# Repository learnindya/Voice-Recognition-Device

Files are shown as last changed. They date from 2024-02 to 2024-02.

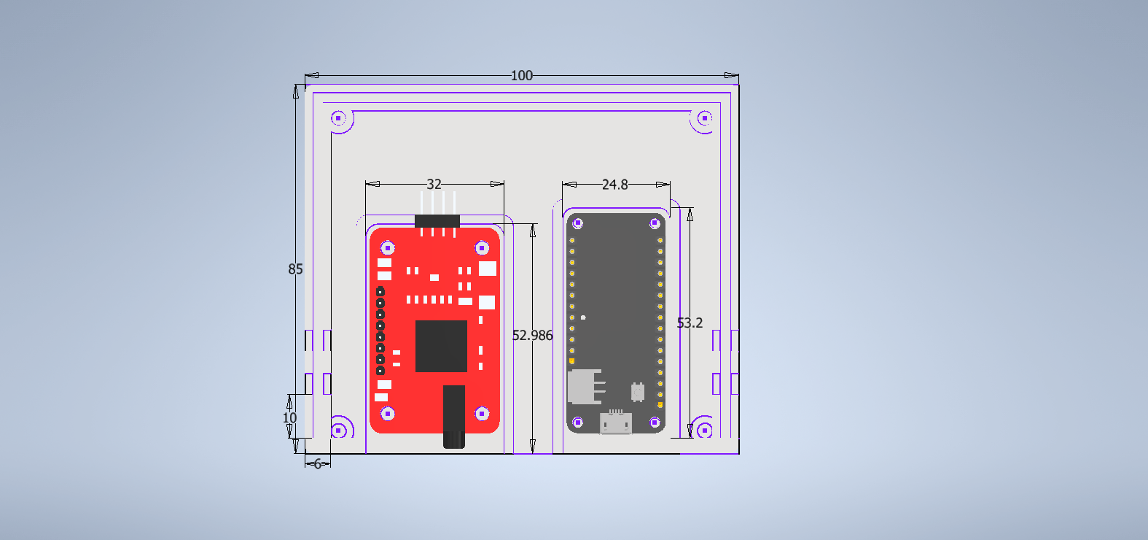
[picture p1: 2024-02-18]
3D drawing/Assembly2 b.png

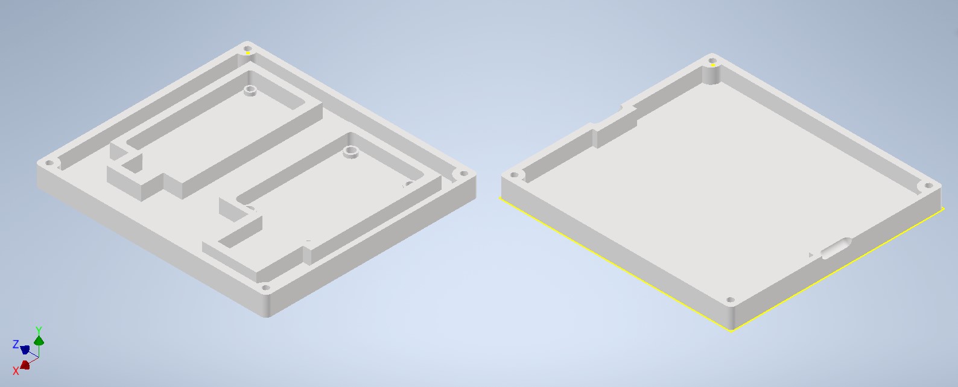
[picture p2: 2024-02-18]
3D drawing/Initial design.jpg

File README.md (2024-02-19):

# Voice-Recognition-Device
Wireless Voice Recognition Interface to Assist People with Tetraplegia to Control their Environment

## Problem
A switch is an essential tool in enabling access to assistive technologies and devices (e.g. Wheelchair controls, mouse clicks on a PC, switch control of electronics, etc.)
Current switch solutions have limitations: Complex mounting. Intrusive. Fragile.
Assistive Technology Manager at Aspire UK wanted to increase the options of accessible switch.

### Requirements from user:
**User Profile**
- Person with tetraplegia 
- No physical movement below neck 
- No speech impairment 
- May be ventilated 
- Assume there is movement of the head but that any head movement will be being used to move a mouse pointer 
- No cognitive impairment

**User Environment**
- Hospital, office
- Home
- Outdoors
- In wheelchair 

**User Acceptance**
- Un-obtrusive, wearable 
- Easy to understand and learn, intuitive to use 
- Minimal set-up needed. Promotes independence. 
- Robust

## Goal
Design a device that enables a person with tetraplegia to trigger a switch action.

## Procedure
1. Send questionnaire and conduct short interview to understand detailed user requirements.
2. Design the electrical diagram, program the modules
3. Assemble the casing and overall device
4. Record instructions
7. Measure the performance
   * Different subjects
   * Different length of commands
   * Different environments
   * Different distance from computer

## Result
- Response to short commands:



Accuracy, sensitivity, precision, prevalence and false positive rate were calculated. For the group testing their own voice (blue column) all values were above 98%. Meanwhile, the result from testing the other’s voice had lower results for all the parameters, and a decrease in respect to increasing distance was visible.

- Response to longer commands:



There was a decrease in all parameters for all subjects compared to short commands. The highest value for testing own’s voice was 94.67%.

- Different environments:



- Different distance from computer:



## Summary
- Price below 100£
- Performance in different environments: Only 6% difference in accuracy and sensitivity
- Battery life 6 hours
- Compatibility with iOS, Windows
- Wireless
- Trigger 6 actions

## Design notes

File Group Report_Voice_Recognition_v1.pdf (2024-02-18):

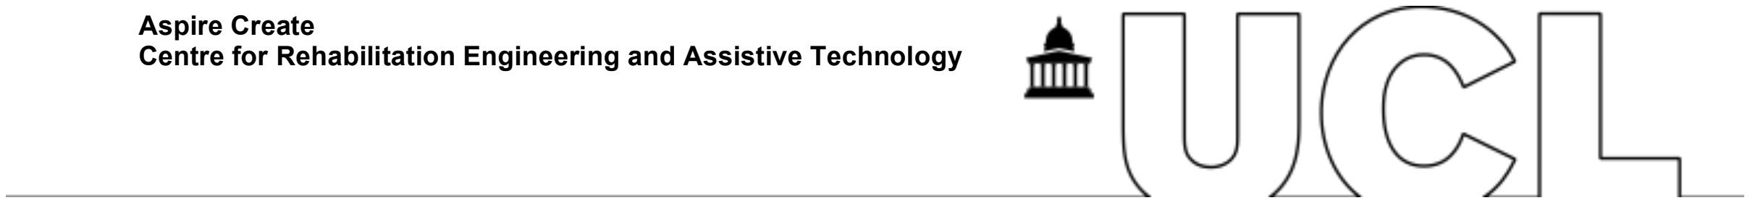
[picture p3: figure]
Aspire Create

University College London
RNOH, Brockley Hill, Stanmore, HA7 4LP, UK www.ucl.ac.uk/aspire-create

Centre for Rehabilitation Engineering and Assistive Technology

# Coursework Submission Coversheet

Student Number (not name!):
18149489, 19153381, 19119482, 19120072

Module Code:

### SURG0094: Group Research Projects

Coursework Title:

### Group Report

### Wireless Voice Recognition Interface to Assist People with Tetraplegia to Control their Environment

Submission Deadline:
11/12/2019 4:00 pm

Word count (include all sections except references/bibliography and appendices. Exclude footnotes, tables, figures, captions, references/bibliography and appendices):
2723

Feedback Request (optional). Please indicate any area(s) of your coursework submission upon which you would particularly like feedback:

NB: I confirm that by submitting this piece of coursework, I have read and understood the UCL statements and guidelines concerning plagiarism.

## UCL Policy on Plagiarism UCL Policy on Late Submission of Coursework

If you are unable to submit on-time due to extenuating circumstances (EC), please refer to

## the UCL Policy on Extenuating Circumstances and contact you’re your programme

administrator as soon as possible.

## UCL Policy on Extenuating Circumstances

## Wireless Voice Recognition Interface to Assist People with Tetraplegia to Control their Environment

A. Anindya (18149489)

1

, A. Khafizova (19120072)¹

, P. Chokpitiboon (19153381)¹

and F. Fries (19119482)¹

Abstract— Around 50% of patients suffering from tetraplegia prefer to stay at home relying on family members or carers to help them complete their daily activities. Despite the efforts to develop control interfaces to simplify their life, it is still hard to find effective products capable to access more than one device at the same time. In this project, we suggest the use of a customizable voice recognition module (VRM) combined with a Bluetooth board to access the computer and potentially a wheelchair. The VRM can store up to 15 commands, which combined, significantly increases the number of devices that can be controlled. In this work, the VRM was characterized to understand how to train the device and find the limitations of the product. The tests showed that the VRM is userdependent, reducing the likelihood of false positives, due to the noise from the environment or words said by someone else. It was also possible to connect to different computers (iOS, Windows) and perform daily tasks such as browsing the internet, opening an email and files, scroll pages up and down, etc. This device shows some interesting potential to aid people suffering from tetraplegia to complete multiple tasks, such as driving a wheelchair, controlling the environment or interface with computers and smartphones.

I. INTRODUCTION

Spinal cord injuries (SCI) affect around 40’000 people in the UK, and for the year 2013-2014, 51% of them are considered to be tetraplegics [1]. Tetraplegia occurs when the the upper cervical level of the spine (C1 to C5) gets damaged, resulting on impairment or complete loss of motor and sensory function below the neck. Due their condition, most of the patients opt to stay at home relying on family members or caregivers to assist them complete their daily activities [2].
Assistive technology is an emerging research area focusing on the development of devices to aid people with any kind of impairments and improve their quality of life. The muscles above the neck of patients suffering from tetraplegia are usually (fully) functional. Therefore, they use them to access computers or smartphones, drive wheelchairs or controlling the environment [3]. A series of switches to serve this purpose have reached the market [4], such as sip and puff switches [5], electromyography sensors [6] and mechanical switches. Moreover, methods like, eye tracking [7], tongue motion [8][9], head tracking [10], sniffing [11] and brain signals [12] have been studied by different research groups. The main problem lies in the management of a significant number of actions, for instance a wheelchair needs at least

1 All students are MSc candidates in Rehabilitation Engineering and Assistive Technologies at University College London (UCL). This project is part of the coursework for SURG0092 Assistive Technology Devices and Rehabilitation Robotics.

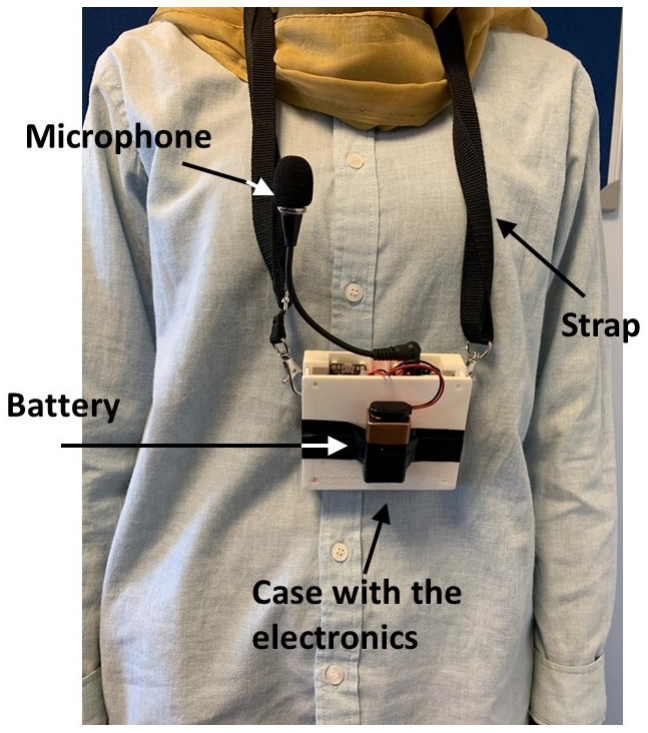
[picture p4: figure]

Fig. 1. User wearing the final prototype. The VRM and the Feather 32u4 are inside the 3D printed box.

five commands to be operated (forward, backwards, left and right, stop) [13]. Unfortunately, the aforementioned methods can saturate when more tasks are combined, thus the interest in more dynamic and efficient methods for hands-free completion of tasks.
An interface that has improved over the years if speech recognition, today it is possible to control (almost) every handheld or computer using speech recognition. However, the most recent devices controlled by voice require access to internet limiting the capabilities of the devices [13]. Nonetheless, voice represents a viable solution to provide patients suffering of tetraplegia with a control interface. Speech has already been used to control wheelchairs [14][15] and more effective algorithms have been develop [13] to enhance their performance. Thus, for this group project we propose the use of a commercial voice recognition module (VRM) capable of recording 15 different commands. The contributions of his work is the characterization of such module and the development of a wireless standalone device capable of aid people with upper limps paralysis to control a computer or a smart phone device. The device design will be described in section II, the methodology and results will be presented in sections III and IV, and the project will be discussed and concluded in sections V and VI respectively.

II. DEVICE DESIGN

A. User Requirements and Product Specifications

The intention was to design a user-oriented prototype, hence, potential end-users were interviewed about their ideas and preferences of the device. This indicated a need to obtain ethical approval before the start of the consultation. Main ethical considerations relate to users’ false expectations of the prototype and confidentiality of the collected data. Since the developed design is a prototype only, a user will not be able to take it home or start using it independently. The number of ethics application is 6860/001 and it was approved by University College London (UCL) Research Ethics Committee. To ensure confidentiality of the obtained data, it was used anonymously in the report. The user requirements were acquired by questionnaire method. There were two questionnaires, one for user and one for family, caregiver and clinician (Appendix ??, and were distributed by email. Due to time constraint, the questionnaires were filled by an assistive technology specialist. The user requirements are presented (Table I).

Parameter | Requirement
Cost Performance Battery Life Physical Design Compatibility Type of communication Minimum Actions | Below 100£ Reliable in different environments 2 to 3 days Inconspicuous iOS, Windows, Android Wireless Trigger 1 action

TABLE I

USER REQUIREMENTS

A set of device specifications listed below were derived from the user requirements:

- Arduino based hardware
- Capable to trigger multiple actions
- Customizable
- Capable to interface with different devices (computer, cellphone, wheelchair, home automation, etc.)
- HID Bluetooth communication protocol
B. Voice Recognition Module
1) Hardware: we purchased an Arduino compatible VRM(Geeetech Voice Recognition, Shenzhen Getech Technology Co.) for this prototype. An image can be seen in Fig. 2, the module can store up to 15 commands in three groups of 5 commands per group. The needed commands have to be recorded on the module first. The module has 4 pins (VCC, GND, Tx, and Rx) to be powered (5V) and to communicate (5V logic) with the environment.
2) Training the voice recognition device: the module is capable to record any kind of commands, as long as it is less than 1.3s long, can be a word or a sentence and it is not language specific. When recording the commands, the entire group has to be recorded at the same time (5 commands), to do so the module has to be accessed through a serial port, we used a UART to USB bridge (CP2102, Silicon Labs). Once the device is accesessed the commands can be recorded. The person recording the commands has to say each command twice to ensure repeatability. If the voice recognition device considers that both pronunciations were identical (or almost the same) the command will be stored, otherwise he will ask to repeat that specific command. The process is repeated for each command until the 5 of them are recorded. After a group is completed it is possible to record the other groups (it is not necessary to record all the commands).

Listing 1. Command examples
/ / Mouse r i g h t c l i c k
b l e . sendCommandCheckOK
( F ( ”AT+BleHi dM o u seB utt o n =R , c l i c k ” ) ) ;

/ / Mouse l e f t c l i c k
b l e . sendCommandCheckOK
( F ( ”AT+BleHi dM o u seB utt o n =L , c l i c k ” ) ) ;

/ / Double c l i c k
b l e . sendCommandCheckOK
( F ( ”AT+BleHi dM o u seB utt o n =L , d o u b l e c l i c k ” ) ) ;

/ / Drag and Drop
b l e . sendCommandCheckOK
( F ( ”AT+BleHi dM o u seB utt o n =L , h ol d , 5 0 0 ” ) ) ;

/ / Read e m ail
b l e . sendCommandCheckOK
( F ( ”AT+BLEHIDCONTROLKEY=EMAILREADER” ) ) ;
C. Electronic Circuit
1) Interface: The entire control interface is composed of different components as depicted in Fig 2. The voice recognition and the Feather have different power requirements, 5V and 3.3V respectively. Two batteries are used to power this prototype, a 9V alkaline battery and a 3.7 LiPo Battery. Therefore, they were not compatible, we solved this problem by adding a logic converter module (Sparkfun Electronics) that converts the 5V logic of the voice recognition to 3.3V logic of the feather, making the data processing possible. A buck converter (Sparkfun Electronics) was used to convert the 9V of the battery to 5V.
2) Software: the software was written in Arduino. When the VRM, detects a command it sends a value between 1-5 (one for each command). The Feather is constantly reading from the serial port, if a value comes in it is passed to a switch statement and the respective command is triggered.

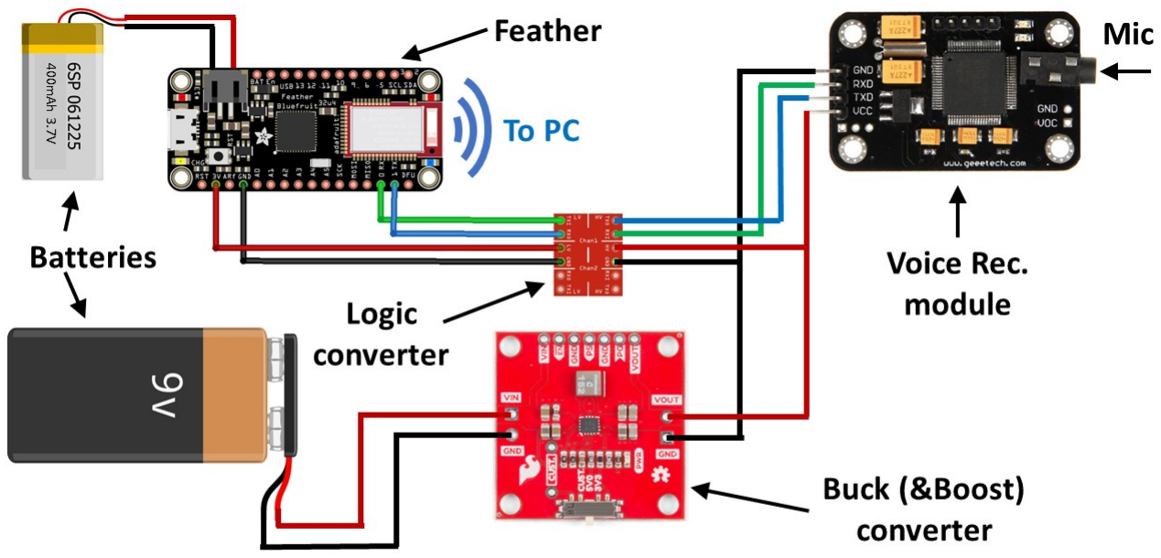
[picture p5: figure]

Fig. 2. Electric diagram of the device. An Feather 32u4 is connected to a VRMthrough a logic converter. The Feather is capable to connect to any Bluettoth device and control it using HID commands. This prototype uses two sources of power.

The used commands were chosen after the characterization,
and are presented in Listing 1:
D. Case Design
To protect the electronics a case comprising a base and a cover, was designed using Autodesk Inventor. On the base, there were two spaces for Feather and the voice recognition module, with adequate space for cables and battery (Fig. 3). The case and its cover was coupled by protruding the cover and extruding the case. There were also screw holes to hold them together. Two supports were made on the left and right sides of the base to attach a strap. Case was printed in Ultimaker 2+ Extended 3D Printer, using acrylonitrile butadiene styrene (ABS). The final product weighed 65 g.

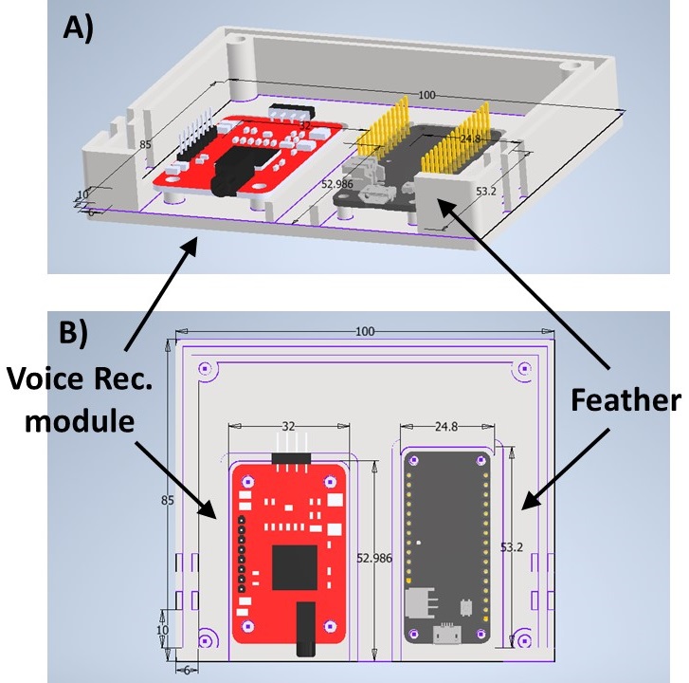
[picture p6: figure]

Fig. 3. CAD assembly of the device with dimensions (the cover is not depicted on this diagram). A) Isometric view. B) Top view.

III. EXPERIMENTS AND PROCEDURES

A. Characterization of the Voice Recognition Module
We performed a characterization of the voice recognition module, to understand its behavior and to be able to optimize the commands that will be implemented in the final prototype. We were interested in measuring the response of the device to different voices. Three subjects (S1, S2 and S3) participated in this experiment. First, the commands were recorded by S1, secondly, the response of the device to all the subjects was measured (including S1). Then the same commands were recorded by S2 and tested by all subjects and same for S3. A total of 15 measurements were taken for each experiment. The VRMwas connected to the computer through an Arduino, the response was displayed on the serial port and the result was recorded manually in Excel. The following experiments were performed:
1) Functional testing: the commands recorded for this experiment were the following:
- “Turn yellow”
- “Turn red”
- “Turn green”
- “Right”
- “Left”
Each command was given 5 times by each subject.
2) Commands length: the experiment was carried as described in the previous test, longer commands were recorded:
- “Turn yellow light on”
- “Turn red light on”
- “Turn green light on”
- “Make a right click”
- “Make a left click”
Each command was given 5 times by each subject.
B. Device Performance
The characterization served to optimize the commands of the final prototype. One subject recorded the commands and all the experiments were carried by that subject. The five commands chosen are sufficient to fully control a computer wirelessly using the device. Each command was given to the VRMand sent to the computer via Bluetooth (through the Feather). As a result an action was triggered on the computer. Same commands were used for the following experiments:
- ”Left mouse”
- ”Right click”
- ”Open file”
- ”Drag and drop”
- ”Email reader”
For all the test each command was given 5 times.
1) Noisy environments: the user repeated each command five times in the following environments:
- Classroom: the device was placed in a classroom with other people and the commands were tested while other people were speaking.
- Street: the device was tested outside the building in a street with cars and people.
- Coffee shop the switch was tested in a coffee shop with music playing and other people speaking.
- Bus stop: the device was taken to a bus stop and was tested with other cars and passengers passing.
- Bar: the device was tested in a relatively noisy environment with the music and other people speaking/screaming.
2) False Positives: the aim of this experiment was to try triggering false positives by giving commands similar to the ones above, two tests were carried:
- Similarity: following commands were given 5 times each:
– ”Left house”
– ”Right blick”
– ”Open smile”
– ”Dark and drop”
– ”Email speeder”
- Only one word of the command: following commands were given 5 times each:
– ”Mouse”
– ”Click”
– ”File”
– ”Drag”
– ”Email”
3) Distance between interface and controlled device: The final prototype was first tested at a distance of 1m and then at a distance of 2m from the computer to observe the strength of a bluetooth connection. Each command was given 5 times.

IV. RESULTS
A. Characterization
1) Functional Testing: the results of the experiment are presented in Fig. 4. Accuracy, sensitivity, precision, prevalence and false positive rate were calculated. For the group testing their own voice (blue column) all values were above 98%. Meanwhile, the result from testing the other’s voice had lower results for all the parameters, and a decrease in respect to increasing distance was visible.

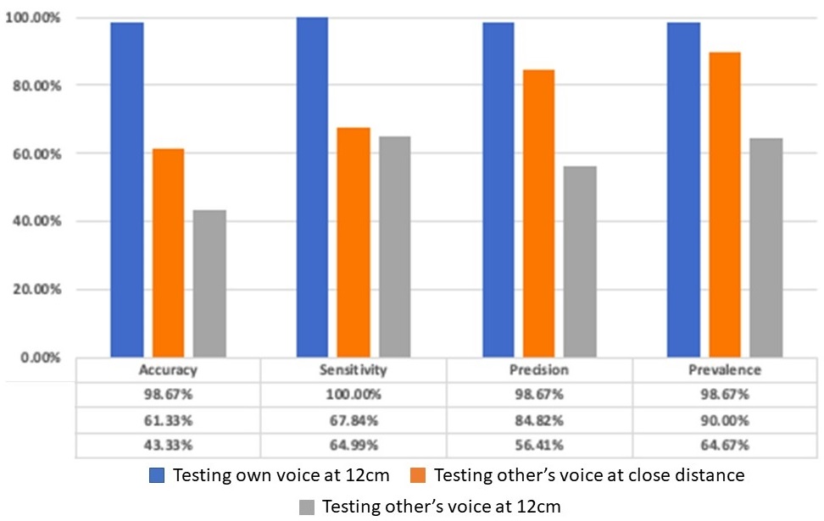
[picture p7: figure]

Fig. 4. Experiment to assess the functionality of the voice recognition module.

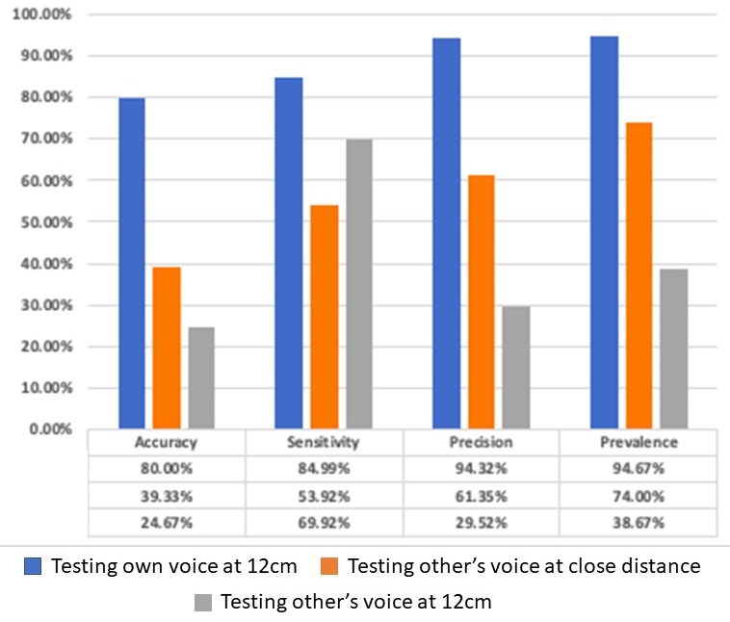
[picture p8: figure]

Fig. 5. Response of the VRMto longer commands.

2) Length of the commands: the results for longest commands are depicted in Fig. 5. The trends are similar to the ones shown in the previous experiment. However, there was a decrease in all parameters for all subjects. The highest value for testing own’s voice was 94.67%. The positives rates dropped significantly for the other’s voice results. Longer commands are more difficult to recognize.
B. Performance

The characterization experiments helped to define the commands for the final prototype. The following experiments were only performed by the subject that recorded the commands.
1) Noisy Environments: the environment experiment was performed and 6 non-controlled environments (street, coffee shop, bus stop, bar). The results of the silent room were compared to the average value from 6 non-controlled environments (Fig. 6). Classroom is slightly higher than that of the non-controlled group in term of accuracy and sensitivity (76% and 70.4% respectively) meanwhile there is no differ-

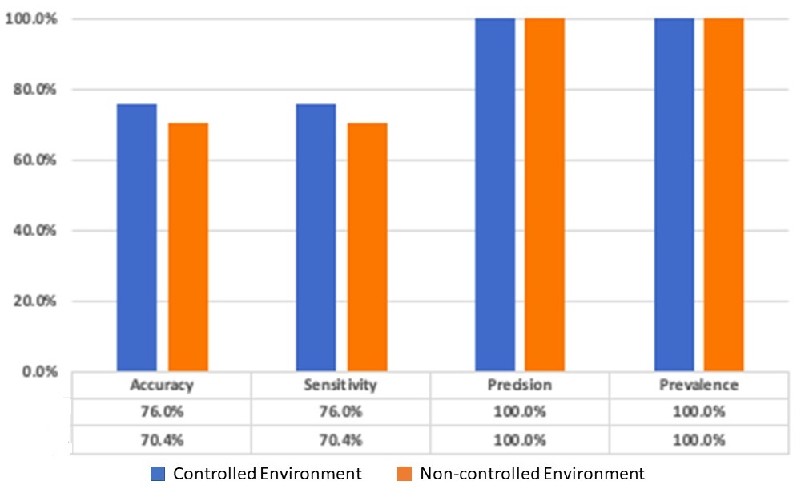
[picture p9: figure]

Fig. 6. Final prototype tested in 6 non controlled environments including street, coffee shop, bus stop, bar.

ence of the precision and prevalence (100% in both group). Trial done at bus stop has highest accuracy and sensitivity (80%) while lowest in the bar (48%). Environments with moderate noise do not affect the performance of the device. Whereas high noise results in an accurate behavior.

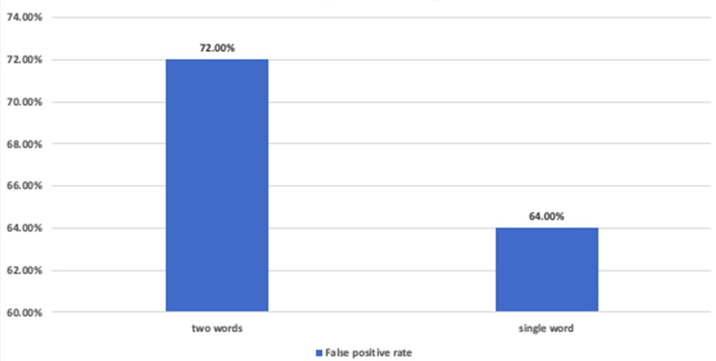
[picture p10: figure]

Fig. 7. After the commands were established. Similar words were given to the edvice to test the sensibility to other or simmilar commands.

2) False Positives: The results of the experiment are depicted in Fig. 7. Two words using similar ending (except drag and drop) showed a higher error rate (72%) than the one of the single similar word (64%). The device is highly sensitive to words similar to the commands, even if only one word of the command is said, the VRMis likely to react.
3) Connection performance: The trial done in 1 metre distance has greater value of accuracy and sensitivity (92%) than the 2 metre trial (88%), whereas, the precision and prevalence reach 100% in both trials as shown in Fig. 8. The experiments show that distance influences the performance of the interface.
V. DISCUSSION
A. Electronic Circuit
A VRMavailable in the market was chosen for this project. Combined with an Arduino based board (Feather 32u4) with Bluetooth capabilities it was possible to develop a wireless interface to control the environment. A series of difficulties arose due the different power requirements of the boards. A logic converter had to be included and the

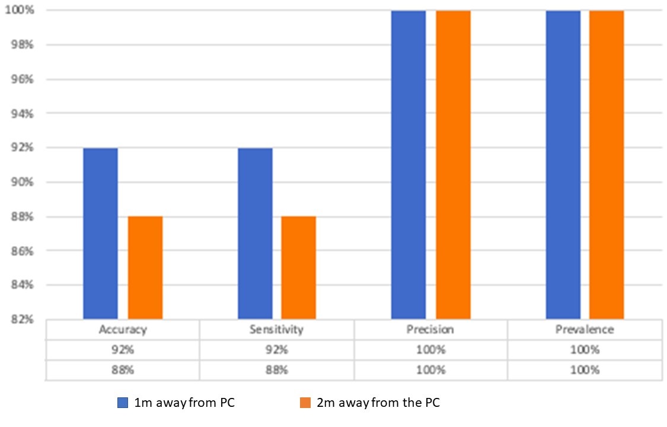
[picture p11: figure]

Fig. 8. User testing the device at different distances from the PC

prototype is currently powered by 2 batteries making the entire device bigger and inefficient. The electronics can be reduced to one printed circuit board (PCB) containing the logic converter and boost converter to power the entire device with one power source. Additionally the PCB would act as link between the Feather and the VRM.

B. Wireless Voice Recognition Interface
A series of tests were carried to study and understand the behavior of the VRM. The characterization experiments showed that shorter commands are more likely to be interpreted correctly by the VRM. Moreover, the device is significantly more responsive if the commands are recorded by the user itself. We also found out that commands need to differ from each other to increase the reliability.
Commands to interface with and control a computer were chosen after the characterization. The reliability of the device was shown in the environment experiment, where the device performed similar in environments with moderate noise. However, we also found out that the use of similar words (or commands) are likely to trigger the device. Reasons for this can be the quality of the microphone. In addition, the voice commands could be filtered to enhance the quality of the command received by the VRM.
The last experiment, indicated that an effective behavior is achieved if the user is close to the device that needs to be controlled. During the experiments we observed that the 3D printed case weakens the signal of the Feather. Therefore, the placement of the board is quite relevant. This can be solved by redesigning the case.

VI. CONCLUSION
Spinal cord injuries affect a significant number of people in the UK (and worldwide), and 51% of them suffer from tetraplegia. Thus, the need to create innovative devices for them to regain their independence and improve the quality of life. Plenty of mechanical switches and interfaces have reached the market, moreover research in this area is beeing supported and progress has been made. Nonetheless, the needs vary from patient to patient and is difficult to find a device suitable for every patient.

For this project we proposed the use of a commercially available VRM, capable to be trained with 15 different commands according to the individual’s requirements. Combined with a Bluetooth device (Feather) it was possible to create an interface to control electronic devices such as the computer hands-free. The experiments showed a high personalized device, likely to respond only to the user regardless of the environment capable to control the computer using 5 simple commands (right and left mouse click, drag and drop, double click and open email). In addition, the device is compatible with iOS and Windows without having to configure it.
In future work we will focus on the improvement of the electronic design, integrating everything into one PCB. This will allow the use of only one rechargeable LiPo battery making the device smaller. The software can also be improved, while it is possible to control the computer, more devices could be included such as wheelchair or the environment (lamps, TV etc.). To achieve this, we need to make use of the 15 commands valaible and be able to jump from one group to an other.

REFERENCES

[1] Spinal injuries association - spinal cord injury charity.
[2] Home page - NSCISC application.
[3] M N Sahadat, Arish Alreja, Nima Mikail, and Maysam Ghovanloo. Comparing the use of single vs. multiple combined abilities in conducting complex computer tasks hands-free. IEEE Transactions on Neural Systems and Rehabilitation Engineering, 2018.
[4] Giulio E. Lancioni, Jeff Sigafoos, Mark F. O’Reilly, and Nirbhay N. Singh. Use of microswitches in habilitation programs. In Assistive Technology, pages 11–40. 2013.
[5] Sip/puff switch.
[6] Sparkfun Electronics . MyoWare muscle sensor kit.
[7] Andreas Bulling and Hans Gellersen. Toward mobile eye-based human-computer interaction. IEEE Pervasive Computing, 2010.
[8] Salman Mohd Khan, Abid Ali Khan, and Omar Farooq. Selection of features and classifiers for EMG/EEG based upper limb assistive devices - a review. IEEE reviews in biomedical engineering, nov 2019.
[9] Lotte N S Andreasen Struijk, Bo Bentsen, Michael Gaihede, and Eugen R Lontis. Error-free text typing performance of an inductive intra-oral tongue computer interface for severely disabled individuals. IEEE Transactions on Neural Systems and Rehabilitation Engineering, pages 2094–2104, 2017.
[10] Ericka Janet Rechy-Ramirez, Huosheng Hu, and Klaus McDonald-Maier. Head movements based control of an intelligent wheelchair in an indoor environment. In 2012 IEEE International Conference on Robotics and Biomimetics (ROBIO). IEEE, 2012.
[11] Anton Plotkin, Lee Sela, Aharon Weissbrod, Roni Kahana, Lior Haviv, Yaara Yeshurun, Nachum Soroker, and Noam Sobel. Sniffing enables communication and environmental control for the severely disabled. Proceedings of the National Academy of Sciences of the United States of America, 2010.
[12] Tom Carlson and Jose del R. Millan. Brain-controlled wheelchairs: A robotic architecture. IEEE Robotics & Automation Magazine, 2013.
[13] Samuel Poirier, Francois Routhier, and Alexandre Campeau-Lecours. Voice control interface prototype for assistive robots for people living with upper limb disabilities. IEEE International Conference on Rehabilitation Robotics : [proceedings], 2019.
[14] Muhammad Tahir Qadri and Syed Ashfaque Ahmed. Voice controlled wheelchair using DSK TMS320C6711. In 2009 International Conference on Signal Acquisition and Processing. IEEE, 2009.
[15] Andrej Skraba, Andrej Kolozvari, Davorin Kofjac, and Radovan Stojanovic. Prototype of speech controlled cloud based wheelchair platform for disabled persons. In 2014 3rd Mediterranean Conference on Embedded Computing (MECO). IEEE, 2014.

### APPENDIX I SURVEY OF ASSISTIVE TECHNOLOGY FOR USER

### 1. What is your age? 20 and below

21 - 30
31 - 40

41 - 50
51 - 60

### above

### 2. Do you live alone or with other people? Living alone Living with people who provide assistance

3. Please indicate if you have difficulty in the following functions.

### Head movement e.g. nodding Eye twitching or blinking Mouth gripping Speaking

### 4. What is your current method to trigger a switch action (e.g. turning on computer)? ___________________________________________________________________ ___________________________________________________________________

### 5. Why did you decide to use the current method? ___________________________________________________________________ ___________________________________________________________________

### 6. What are your main factors in choosing an assistive technology to trigger a switch action? ___________________________________________________________________ ___________________________________________________________________

7. What kind of actions do you want to trigger by assistive technology? (e.g. texting,

### calling, sending commands to wheelchair) ___________________________________________________________________ ___________________________________________________________________

### 8. What do you think about using touch sensor to trigger a switch action? ___________________________________________________________________ ___________________________________________________________________

### 9. How often do you think the assistive device should be charged?

### _____________________________________________________hours/days

### 10. How much do you expect a touch sensor to cost? ___________________________________________________________________

11. What do you think of other assistive technology to trigger a switch action, e.g. voice

### recognition device? ___________________________________________________________________ ___________________________________________________________________

### SURVEY OF ASSISTIVE TECHNOLOGY FOR RELATIVES AND CLINICIANS

### 1. Please indicate who is completing this survey

### PaWieQW¶V famil\ Caregiver Doctor Other health professional, please specify: _________

### 2. Does tetraplegic patient require any assistance from you? Yes

If yes, please indicate the activities that require your assistance.

### ______________________________________________________________

No

### If no, is there any other form of assistance for the patient? ______________________________________________________________

### 3. Based on your experience, what is the best assistive technology to trigger a switch action? ___________________________________________________________________ ___________________________________________________________________

### 4. What do you consider in choosing an assistive technology to trigger a switch action for your patient/relative? ___________________________________________________________________ ___________________________________________________________________

### 5. What do you think about using touch sensor to trigger a switch action? ___________________________________________________________________ ___________________________________________________________________

### 6. How often do you think the assistive device should be charged?

### _____________________________________________________hours/days

### 7. How much do you expect a touch sensor to cost? ___________________________________________________________________

### 8. What do you think of other assistive technology to trigger a switch action, e.g. voice recognition device? ___________________________________________________________________ ___________________________________________________________________

### APPENDIX II SURVEY OF ASSISTIVE TECHNOLOGY FOR USER - FILLED

### 1. What is your age?

### x 20 and below x 21 - 30

x 31 - 40

### 2. Do you live alone or with other people? x Living alone

x 41 - 50 x 51 - 60

### x above

### x Living with people who provide assistance YES

3. Please indicate if you have difficulty in the following functions. x Head movement e.g. nodding x Eye twitching or blinking x Mouth gripping

### x Speaking

### 4. What is your current method to trigger a switch action (e.g. turning on computer)?

None

### 5. Why did you decide to use the current method?

n/a

### 6. What are your main factors in choosing an assistive technology to trigger a switch action?

Reliability and consistency. Inconspicuous.

7. What kind of actions do you want to trigger by assistive technology? (e.g. texting,

### calling, sending commands to wheelchair) Could be a number of possible uses. If it is easy to operate then I think it would have a wide application

### 8. What do you think about using touch sensor to trigger a switch action?

Depends on the way I would need to touch the device.

### 9. How often do you think the assistive device should be charged? Every 2-3 days hours/days

### 10. How much do you expect a touch sensor to cost?

<£100

11. What do you think of other assistive technology to trigger a switch action, e.g. voice

### recognition device?

OK providing it meets other criteria._

### SURVEY OF ASSISTIVE TECHNOLOGY FOR RELATIVES AND CLINICIANS - FILLED

### 1. Please indicate who is completing this survey

### x Patient’s family x Caregiver x Doctor x Other health professional, please specify: Assistive Technology Specialist

### 1. Does tetraplegic patient require any assistance from you? x Yes

If yes, please indicate the activities that require your assistance.

### Help with selection of Assistive devices for computer access

### x No If no, is there any other form of assistance for the patient?

### 3. Based on your experience, what is the best assistive technology to trigger a switch action? It depends in what context the switch is being used and what movement is available

to the user. With a high level injury there are limited options available.

### 4. What do you consider in choosing an assistive technology to trigger a switch action for your patient/relative?

Reliability and consistency oil operation. Inconspicuous.

### 5. What do you think about using touch sensor to trigger a switch action?

I am unable to touch with my hands - it would depend on how I am able to ac5vate it.

### 6. How often do you think the assistive device should be charged?

Once every 2-3 days would be best.

### hours/days

### 7. How much do you expect a touch sensor to cost?

If it does the job well than it will be worth a premium price. Typically switches should be <£100

### 8. What do you think of other assistive technology to trigger a switch action, e.g. voice recognition device?

Voice is fine, providing it is reliable and consistent and I can use independently.

### APPENDIX III RESULTS OF EXPERIMENT 1 TESTING SHORT COMMANDS BY DIFFERENT SUBJECTS: FUNCTIONAL TESTING

Test № | Voice owner | Tester | Testing distance | Trial | Commands
Turn yellow | Turn red | Turn green | Right | Left
1 | S1 | S1 | 12 cm | 1 | + | + | + | + | +
| | | | 2 | + | + | + | + | -
| | | | 3 | + | + | + | + | +
| | | | 4 | + | + | + | + | +
| | | | 5 | + | + | + | + | +
2 | S1 | S3 | 12 cm | 1 | -(red) | + | + | + | -
| | | | 2 | - | + | - | + | -
| | | | 3 | -(red) | + | - | - | -
| | | | 4 | -(red) | + | + | + | -
| | | | 5 | -(red) | + | - | + | -
3 | S1 | S2 | 12 cm | 1 | - | - | - | - | +
| | | | 2 | - | - | - | -(left) | +
| | | | 3 | - | - | - | -(greeen) | -(right)
| | | | 4 | - | - | - | -(yellow) | -(right)
| | | | 5 | - | - | - | -(left) | -(right)
4 | S1 | S3 | As close as possible | 1 | + | + | + | -(red) | +
| | | | 2 | + | + | -(noic e) | + | +
| | | | 3 | -(red) | + | + | + | +
| | | | 4 | - | + | + | + | -(right)
| | | | 5 | + | + | - | + | -(right)
5 | S1 | S2 | As close as possible | 1 | -(right) | -(left) | + | -(left) | -(right)
| | | | 2 | - | -(left) | + | -(yellow) | +
| | | | 3 | - | -(left) | -(left) | -(left) | +
| | | | 4 | -(left) | -(right) | -(left) | -(left) | +
| | | | 5 | - | -(right) | -(right ) | + | +
6 | S2 | S2 | 12 cm | 1 | + | + | + | + | +
| | | | 2 | + | + | + | + | +
| | | | 3 | + | + | + | + | +
| | | | 4 | + | + | + | + | +
| | | | 5 | + | + | + | + | +
7 | S2 | S3 | 12 cm | 1 | + | - | -(red) | + | -
| | | | 2 | - | - | + | - | -
| | | | 3 | - | - | + | + | -
| | | | 4 | - | - | + | - | -
| | | | 5 | - | - | + | + | -
8 | S2 | S1 | 12 cm | 1 | + | - | + | -(left) | +
| | | | 2 | - | - | + | -(left) | +

3 | - | - | + | -(left) | +
4 | - | - | + | -(left) | +
5 - | | -(green) | + | -(left) | +
9 | S2 | S3 | As close as possible | 1 | -(red) | + | + | + | +
| | | | 2 | + | + | -(red) | + | +
| | | | 3 | + | + | + | + | +
| | | | 4 | + | + | -(red) | + | +
| | | | 5 | + | + | + | + | +
10 | S2 | S1 | As close as possible | 1 | -(green) | + | + | -(left) | +
| | | | 2 | + | + | + | -(left) | +
| | | | 3 | + | + | + | + | +
| | | | 4 | + | + | + | -(left) | +
| | | | 5 | + | + | + | + | +
11 | S3 | S3 | 12 cm | 1 | + | + | + | + | +
| | | | 2 | + | + | + | + | +
| | | | 3 | + | + | + | + | +
| | | | 4 | + | + | + | + | +
| | | | 5 | + | + | + | + | +
12 | S3 | S2 | 12 cm | 1 | + | + | - | + | +
| | | | 2 | -(red) | + | -(left) | + | +
| | | | 3 | -(red) | -right | + | + | +
| | | | 4 | -(red) | -(left) | -(left) | + | +
| | | | 5 | -(red) | -(left) | + | + | +
13 | S3 | S1 | 12 cm | 1 | -(red) | + | -(red) | + | +
| | | | 2 | + | + | + | + | -(right)
| | | | 3 | + | - | - | + | -(right)
| | | | 4 | + | + | + | + | +
| | | | 5 + | | -(green) | + | + | +
14 | S3 | S2 | As close as possible | 1 | - | + | + | + | +
| | | | 2 | - | -(right) | + | -(left) | +
| | | | 3 | -(red) | -(left) | -(left) | -(left) | +
| | | | 4 | -(left) | -(left) | + | + | +
| | | | 5 | - | -(left) | -(red) | -(left) | +
15 | S3 | S1 | As close as possible | 1 | -(left) | + | -(red) | + | +
| | | | 2 | + | - | -(red) | + | +
| | | | 3 | + | - | -(red) | + | +
| | | | 4 + | | -(yellow ) | + | -(left) | -(right)
| | | | 5 | + | + | - | -(left) | +

### APPENDIX IV RESULTS OF EXPERIMENT 2 TESTING LONG COMMANDS BY DIFFERENT SUBJECTS: COMMAND LENGTHS

Test № | Voice owner | Tester | Testing distance | Trial | Commands
Turn the yellow light on | Turn the red light on | Turn the green light on | Make a right click | Make a left click
1 | S1 | S1 | 12 cm | 1 | -(red) | + | + | - (make a left click) | +
| | | | 2 | -(red) | + | + | - (make a left click) | +
| | | | 3 | -(red) | + | + | - (make a left click) | +
| | | | 4 | + | + | + | - (make a left click) | +
| | | | 5 | + | + | + | - (make a left click) | +
2 | S1 | S4 | 12 cm | 1 | - | + | - | - (make a left click) | +
| | | | 2 | - | - | - | - | -
| | | | 3 | - | - | - | - (make a left click) | -
| | | | 4 | + | - | + | - (make a left click) | +
| | | | 5 | - | - | - | - (make a left click) | +
3 | S1 | S2 | 12 cm | 1 | - | - | - | - | +
| | | | 2 | - | + | - | - | -
| | | | 3 | - | - | + | - | -
| | | | 4 | - | - | - | - | -
| | | | 5 | - | - | + | - | -
4 | S1 | S4 | As close as possible | 1 | - | - | -(make a right click) | - (make a left click) | +
| | | | 2 - | | -(make a left click) | -(make a left click) | - (make a left click) | +
| | | | 3 | + | -(green) | - | - (make a left click) | -
| | | | 4 - | | -(make a left click) | - | - (make a left click) | +
| | | | 5 | + | - | - | - (make a left click) | +
5 | S1 | S2 | As close as possible | 1 | -(make a left click) | -(green) | - | - (make a left click) | +
| | | | 2 | - | - | + | - (make a left click) | +
| | | | 3 | - | - | + | - | +
| | | | 4 | - | - | -(make a left click) | - (make a left click) | +

5 | - | - | +

### - (make a

left click) | +
6 | S2 | S2 | 12 cm | 1 | -(red) | + | + | + | +
| | | | 2 | + | + | + | + | +
| | | | 3 | + | + | + | + | +
| | | | 4 | - | -(green) | + | + | +
| | | | 5 | - | + | + | + | +
7 | S2 | S4 | 12 cm | 1 | -(green) | - | + | + | -(make a right click)
| | | | 2 - | | -(make a right click) | + | + | -(make a right click)
| | | | 3 | - | - | - | + | -(make a right click)
| | | | 4 | - | - | + | + | -
| | | | 5 | - | - | + | + | -
8 | S2 | S1 | 12 cm | 1 | -(red) | + | - | - | +
| | | | 2 | -(green) | + | - | - | +
| | | | 3 | - | + | - | - | +
| | | | 4 | - | - | - | - | -
| | | | 5 | -(red) | - | - | - | -
9 | S2 | S4 | As close as possible | 1 | -(red) | + | - | + | -(make a right click)
| | | | 2 -(red) | | -(make a right click) | -(make a right click) | + | -(make a right click)
| | | | 3 | - | + | -(make a right click) | + | -(make a right click)
| | | | 4 | - | + | -(make a right click) | + | -(make a right click)
| | | | 5 | - | + | + | + | +
10 | S2 | S1 | As close as possible | 1 | - | + | -(red) | + | -
| | | | 2 | - | + | -(red) | + | -(make a right click)
| | | | 3 | -(red) | + | + | + | -(make a right click)
| | | | 4 | - | + | -(red) | + | +
| | | | 5 | - | - | -(red) | + | +
11 | S4 | S4 | 12 cm | 1 | + | -(green) | + | - | +
| | | | 2 | + | + | + | + | +
| | | | 3 | + | + | + | + | +
| | | | 4 | + | + | + | + | +
| | | | 5 | + | - | + | + | +
12 | S4 | S2 | 12 cm | 1 | - | + | - | - | -
| | | | 2 | - | + | - | + | +

3 | - | - | - | - | -
4 | - | + | - | - | -
5 | - | + | - | - | -(make a right click)
13 | S4 | S1 | 12 cm | 1 | + | -(yellow) | -(yellow) | - | -
| | | | 2 | - | -(yellow) | -(yellow) | - | -
| | | | 3 | + | - | -(yellow) | - (make a left click) | -
| | | | 4 | + | - | -(yellow) | - | +
| | | | 5 | + | -(yellow) | - | - | +
14 | S4 | S2 | As close as possible | 1 | - | + | + | - | +
| | | | 2 | - | + | -(yellow) | + | +
| | | | 3 | - | + | - | + | +
| | | | 4 | - | + | - | - (make a left click) | -(make a right click)
| | | | 5 | + | + | - | + | +
15 | S4 | S1 | As close as possible | 1 | + | -(yellow) | -(yellow) | - | +
| | | | 2 | + | - | -(yellow) | - (make a left click) | -(make a right click)
| | | | 3 | + | -(yellow) | -(yellow) | - (make a left click) | +
| | | | 4 | + | -(yellow) | -(yellow) | - (make a left click) | -(make a right click)
| | | | 5 | + | -(yellow) | -(yellow) | - (make a left click) | +

### APPENDIX V RESULTS OF EXPERIMENT 3: ENVIRONMENTAL TESTING

### Quiet environment

### Street

№ trial | Left mouse | Right click | Open file | Drag and drop | Email reader
1 | + | + | - | + | +
2 | + | + | - | + | +
3 | + | + | + | + | +
4 | - | - | + | + | +
5 | + | - | - | + | +

### Coffee shop

№ trial | Left mouse | Right click | Open file | Drag and drop | Email reader
1 | + | + | - | + | +
2 | + | - | + | - | +
3 | + | - | + | - | +
4 | + | + | + | + | +
5 | + | - | + | + | +

### Bus stop

№ trial | Left mouse | Right click | Open file | Drag and drop | Email reader
1 | + | + | + | + | +
2 | + | + | + | + | +
3 | - | - | + | + | +
4 | - | - | + | + | -
№ trial | Left mouse | Right click | Open file | Drag n drop | Email reader
1 | + | + | + | + | +
2 | - | - | - | - | +
3 | + | - | + | + | +
4 | + | + | + | + | +
5 | + | - | + | + | +

5 | + | + | + | + | +

### Bar

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

### Classroom

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

### APPENDIX VI RESULTS OF EXPERIMENT 4: FALSE POSITIVE TESTING

№ trial | Left house | Right blick | Open smile | Dark and drop | Email speeder
1 | - | - | + | + | +
2 | - | + | + | + | +
3 | + | - | + | + | +
4 | + | - | - | + | +
5 | + | + | + | - | +
№ trial | Mouse | Click | File | Drag | Email
1 | + | + | - | -(right click) | +
2 | + | + | - | -(right click) | -
3 | + | + | + | -(right click) | -
4 | + | + | - | - | -
5 | + | + | - | -(right click) | -

### APPENDIX VII RESULTS OF EXPERIMENT 5: DISTANCE TESTING

### Distance - bluetooth 1m

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

### Distance – bluetooth 2m

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

### APPENDIX VIII DATA COLLECTION AND DATA ANALYSIS OF EXPERIMENT 1: FUNCTIONAL TESTING

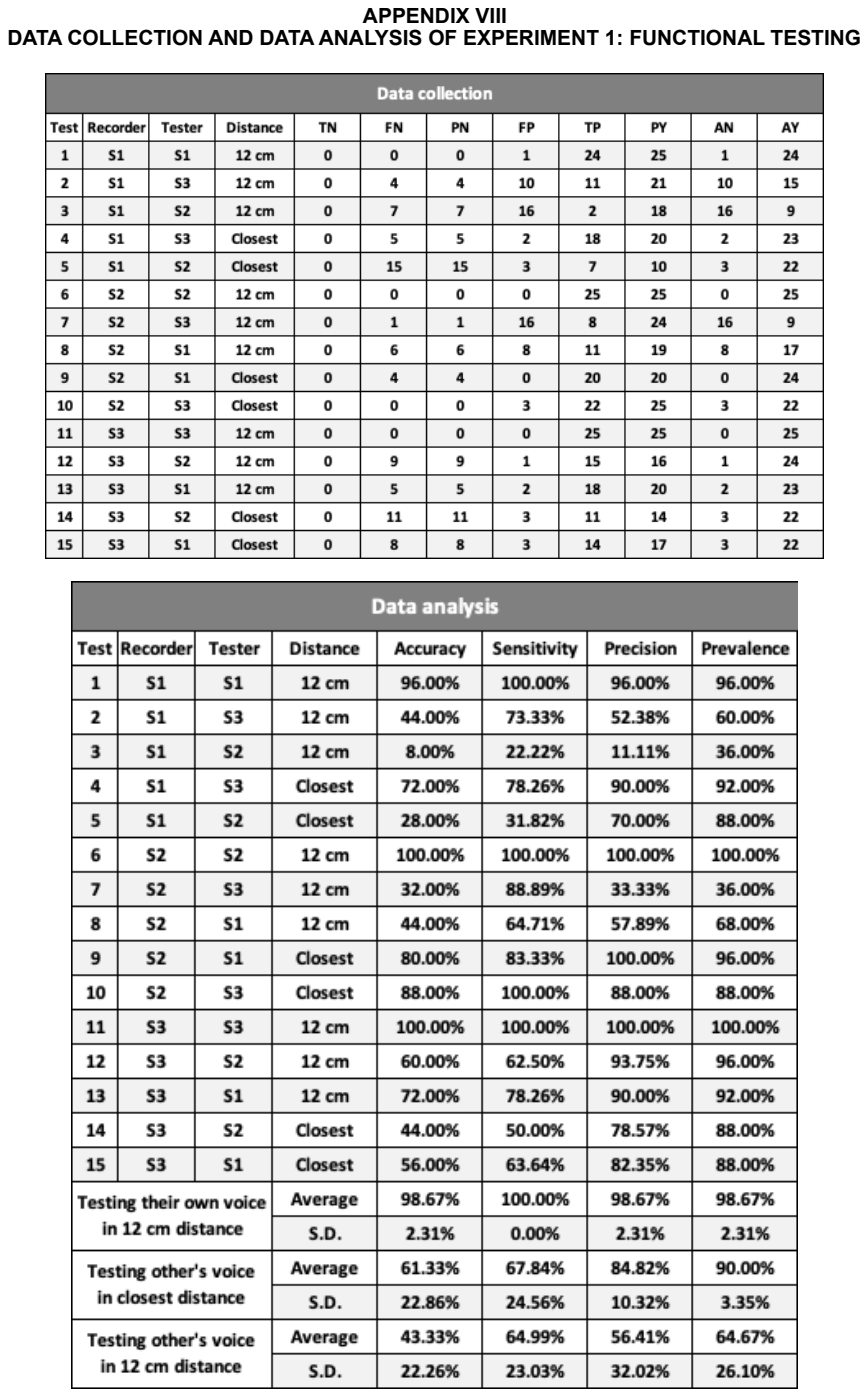
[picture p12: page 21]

### APPENDIX IX DATA COLLECTION AND DATA ANALYSIS OF EXPERIMENT 2: COMMAND LENGTHS

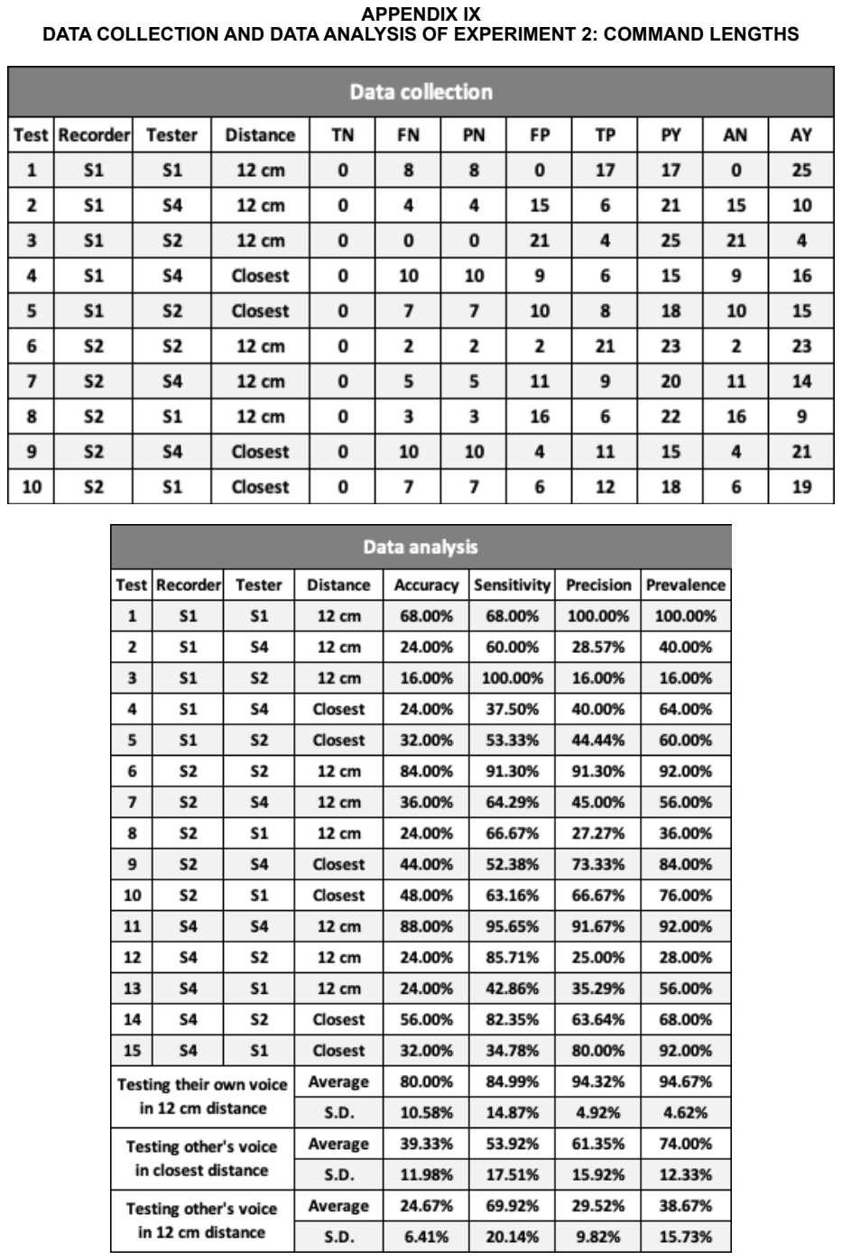
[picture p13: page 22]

### APPENDIX X DATA COLLECTION AND DATA ANALYSIS OF EXPERIMENT 3: ENVIRONMENTAL TESTING

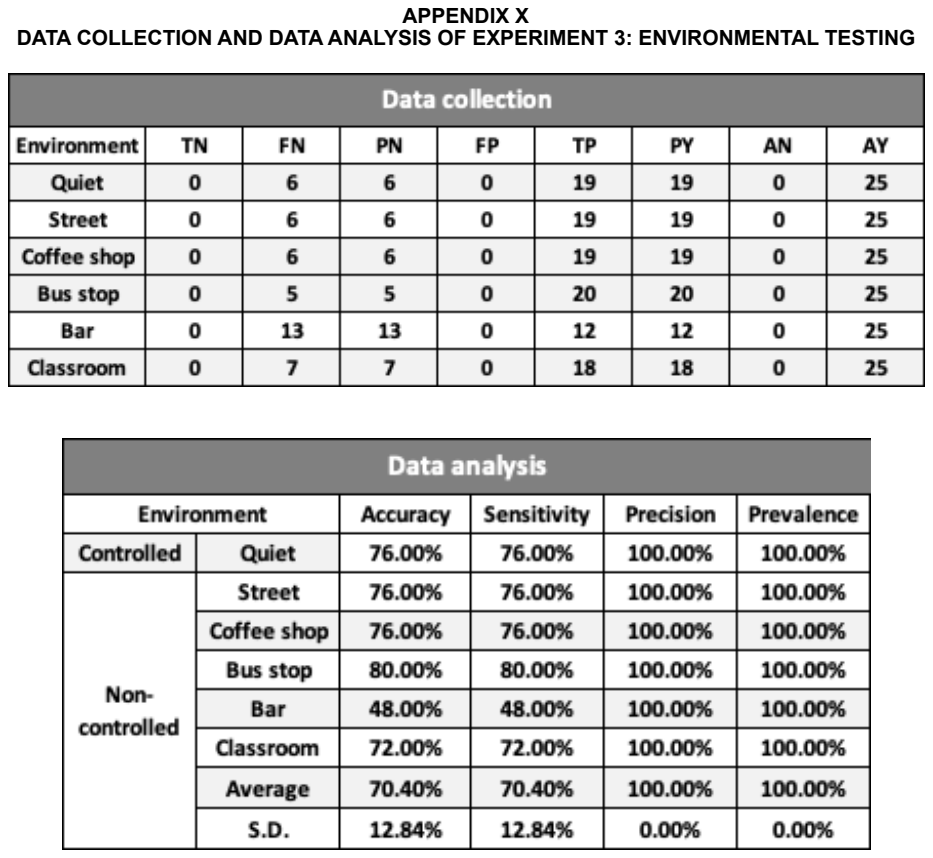
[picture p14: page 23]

### APPENDIX XI DATA COLLECTION AND DATA ANALYSIS OF EXPERIMENT 4: FALSE POSITIVE TESTING

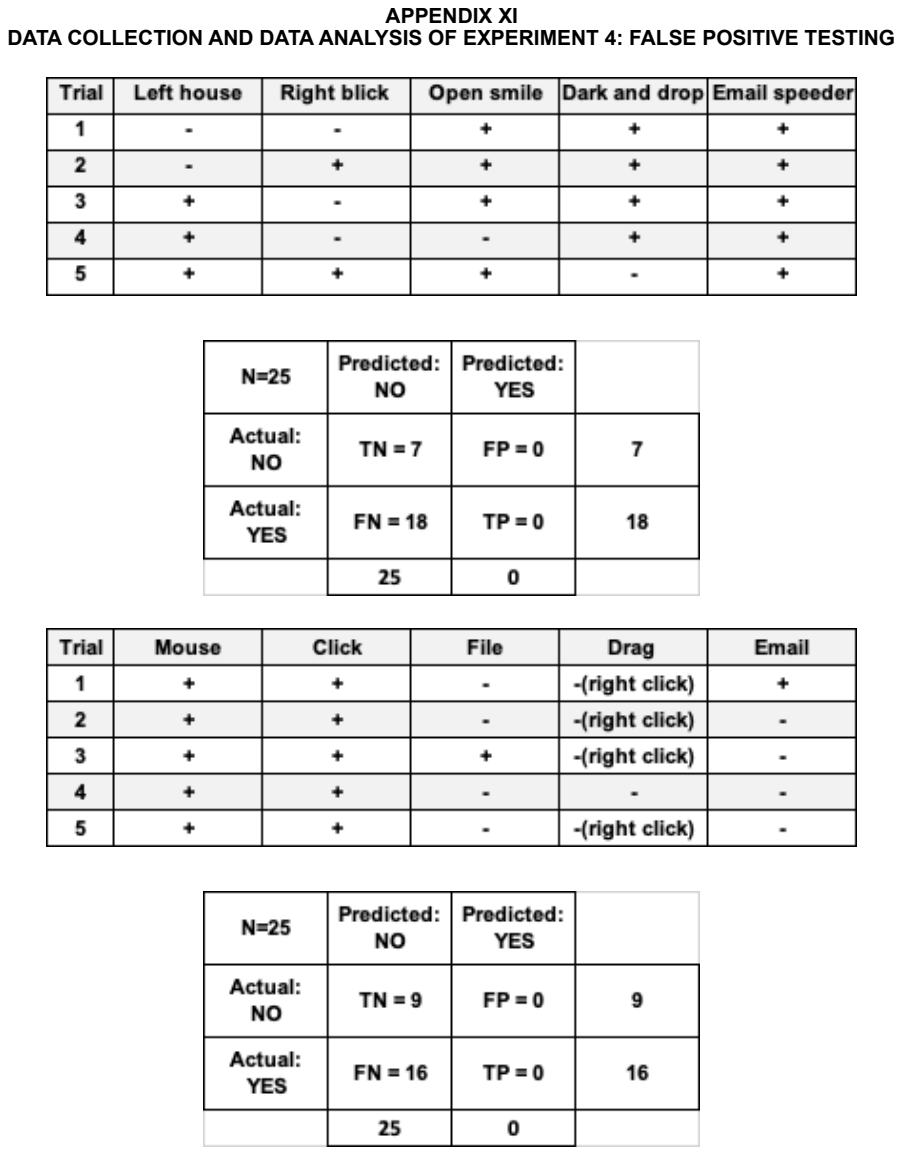
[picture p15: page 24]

### APPENDIX XII DATA COLLECTION AND DATA ANALYSIS OF EXPERIMENT 5: DISTANCE TESTING

### APPENDIX XI DATA COLLECTION AND DATA ANALYSIS OF EXPERIMENT 4: FALSE POSITIVE TESTING

### APPENDIX XII DATA COLLECTION AND DATA ANALYSIS OF EXPERIMENT 5: DISTANCE TESTING

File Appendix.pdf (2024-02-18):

APPENDIX I
SURVEY OF ASSISTIVE TECHNOLOGY FOR USER
1. What is your age?
20 and below
21 - 30
31 - 40

41 - 50
51 - 60
above
2. Do you live alone or with other people?
Living alone
Living with people who provide assistance
3. Please indicate if you have difficulty in the following functions. Head movement e.g. nodding
Eye twitching or blinking
Mouth gripping
Speaking
4. What is your current method to trigger a switch action (e.g. turning on computer)? ___________________________________________________________________ ___________________________________________________________________
5. Why did you decide to use the current method? ___________________________________________________________________ ___________________________________________________________________
6. What are your main factors in choosing an assistive technology to trigger a switch action?
___________________________________________________________________ ___________________________________________________________________
7. What kind of actions do you want to trigger by assistive technology? (e.g. texting, calling, sending commands to wheelchair) ___________________________________________________________________ ___________________________________________________________________
8. What do you think about using touch sensor to trigger a switch action? ___________________________________________________________________ ___________________________________________________________________
9. How often do you think the assistive device should be charged?

_____________________________________________________hours/days

10. How much do you expect a touch sensor to cost? ___________________________________________________________________
11. What do you think of other assistive technology to trigger a switch action, e.g. voice recognition device?
___________________________________________________________________ ___________________________________________________________________

SURVEY OF ASSISTIVE TECHNOLOGY FOR RELATIVES AND CLINICIANS

1. Please indicate who is completing this survey

PaWieQW¶V famil\
Caregiver
Doctor
Other health professional, please specify: _________
2. Does tetraplegic patient require any assistance from you?
Yes
If yes, please indicate the activities that require your assistance. ______________________________________________________________

No
If no, is there any other form of assistance for the patient? ______________________________________________________________
3. Based on your experience, what is the best assistive technology to trigger a switch action?
___________________________________________________________________ ___________________________________________________________________
4. What do you consider in choosing an assistive technology to trigger a switch action for your patient/relative? ___________________________________________________________________ ___________________________________________________________________
5. What do you think about using touch sensor to trigger a switch action? ___________________________________________________________________ ___________________________________________________________________
6. How often do you think the assistive device should be charged?

_____________________________________________________hours/days

7. How much do you expect a touch sensor to cost? ___________________________________________________________________
8. What do you think of other assistive technology to trigger a switch action, e.g. voice recognition device?
___________________________________________________________________ ___________________________________________________________________

APPENDIX II
SURVEY OF ASSISTIVE TECHNOLOGY FOR USER - FILLED
1. What is your age?
x 20 and below x 21 - 30

x 31 - 40

2. Do you live alone or with other people? x Living alone

x 41 - 50 x 51 - 60

x above

x Living with people who provide assistance YES

3. Please indicate if you have difficulty in the following functions. x Head movement e.g. nodding x Eye twitching or blinking x Mouth gripping

x Speaking

4. What is your current method to trigger a switch action (e.g. turning on computer)? None
5. Why did you decide to use the current method?
n/a
6. What are your main factors in choosing an assistive technology to trigger a switch action?
Reliability and consistency. Inconspicuous.
7. What kind of actions do you want to trigger by assistive technology? (e.g. texting, calling, sending commands to wheelchair)
Could be a number of possible uses. If it is easy to operate then I think it would have a wide application
8. What do you think about using touch sensor to trigger a switch action?
Depends on the way I would need to touch the device.
9. How often do you think the assistive device should be charged? Every 2-3 days
hours/days
10. How much do you expect a touch sensor to cost?
<£100
11. What do you think of other assistive technology to trigger a switch action, e.g. voice recognition device?
OK providing it meets other criteria._

SURVEY OF ASSISTIVE TECHNOLOGY FOR RELATIVES AND CLINICIANS - FILLED

1. Please indicate who is completing this survey
x Patient’s family
x Caregiver x Doctor

x Other health professional, please specify: Assistive Technology Specialist

1. Does tetraplegic patient require any assistance from you?
x Yes
If yes, please indicate the activities that require your assistance. Help with selection of Assistive devices for computer access

x No
If no, is there any other form of assistance for the patient?
3. Based on your experience, what is the best assistive technology to trigger a switch action?
It depends in what context the switch is being used and what movement is available to the user. With a high level injury there are limited options available.
4. What do you consider in choosing an assistive technology to trigger a switch action for your patient/relative?
Reliability and consistency oil operation. Inconspicuous.
5. What do you think about using touch sensor to trigger a switch action?
I am unable to touch with my hands - it would depend on how I am able to ac5vate it.
6. How often do you think the assistive device should be charged?
Once every 2-3 days would be best.
hours/days
7. How much do you expect a touch sensor to cost?
If it does the job well than it will be worth a premium price. Typically switches should be <£100
8. What do you think of other assistive technology to trigger a switch action, e.g. voice recognition device?
Voice is fine, providing it is reliable and consistent and I can use independently.

APPENDIX III
RESULTS OF EXPERIMENT 1 TESTING SHORT COMMANDS BY DIFFERENT SUBJECTS: FUNCTIONAL TESTING
Test № | Voice owner | Tester | Testing distance | Trial | Commands
Turn yellow | Turn red | Turn green | Right | Left
1 | S1 | S1 | 12 cm | 1 | + | + | + | + | +
| | | | 2 | + | + | + | + | -
| | | | 3 | + | + | + | + | +
| | | | 4 | + | + | + | + | +
| | | | 5 | + | + | + | + | +
2 | S1 | S3 | 12 cm | 1 | -(red) | + | + | + | -
| | | | 2 | - | + | - | + | -
| | | | 3 | -(red) | + | - | - | -
| | | | 4 | -(red) | + | + | + | -
| | | | 5 | -(red) | + | - | + | -
3 | S1 | S2 | 12 cm | 1 | - | - | - | - | +
| | | | 2 | - | - | - | -(left) | +
| | | | 3 | - | - | - | -(greeen) | -(right)
| | | | 4 | - | - | - | -(yellow) | -(right)
| | | | 5 | - | - | - | -(left) | -(right)
4 | S1 | S3 | As close as possible | 1 | + | + | + | -(red) | +
| | | | 2 | + | + | -(noic e) | + | +
| | | | 3 | -(red) | + | + | + | +
| | | | 4 | - | + | + | + | -(right)
| | | | 5 | + | + | - | + | -(right)
5 | S1 | S2 | As close as possible | 1 | -(right) | -(left) | + | -(left) | -(right)
| | | | 2 | - | -(left) | + | -(yellow) | +
| | | | 3 | - | -(left) | -(left) | -(left) | +
| | | | 4 | -(left) | -(right) | -(left) | -(left) | +
| | | | 5 | - | -(right) | -(right ) | + | +
6 | S2 | S2 | 12 cm | 1 | + | + | + | + | +
| | | | 2 | + | + | + | + | +
| | | | 3 | + | + | + | + | +
| | | | 4 | + | + | + | + | +
| | | | 5 | + | + | + | + | +
7 | S2 | S3 | 12 cm | 1 | + | - | -(red) | + | -
| | | | 2 | - | - | + | - | -
| | | | 3 | - | - | + | + | -
| | | | 4 | - | - | + | - | -
| | | | 5 | - | - | + | + | -
8 | S2 | S1 | 12 cm | 1 | + | - | + | -(left) | +
| | | | 2 | - | - | + | -(left) | +

3

+

-(left)

+
4 | - | - | + | -(left) | +
5 | - | -(green) | + | -(left) | +
9 | S2 | S3 | As close as possible | 1 | -(red) | + | + | + | +
| | | | 2 | + | + | -(red) | + | +
| | | | 3 | + | + | + | + | +
| | | | 4 | + | + | -(red) | + | +
| | | | 5 | + | + | + | + | +
10 | S2 | S1 | As close as possible | 1 | -(green) | + | + | -(left) | +
| | | | 2 | + | + | + | -(left) | +
| | | | 3 | + | + | + | + | +
| | | | 4 | + | + | + | -(left) | +
| | | | 5 | + | + | + | + | +
11 | S3 | S3 | 12 cm | 1 | + | + | + | + | +
| | | | 2 | + | + | + | + | +
| | | | 3 | + | + | + | + | +
| | | | 4 | + | + | + | + | +
| | | | 5 | + | + | + | + | +
12 | S3 | S2 | 12 cm | 1 | + | + | - | + | +
| | | | 2 | -(red) | + | -(left) | + | +
| | | | 3 | -(red) | -right | + | + | +
| | | | 4 | -(red) | -(left) | -(left) | + | +
| | | | 5 | -(red) | -(left) | + | + | +
13 | S3 | S1 | 12 cm | 1 | -(red) | + | -(red) | + | +
| | | | 2 | + | + | + | + | -(right)
| | | | 3 | + | - | - | + | -(right)
| | | | 4 | + | + | + | + | +
| | | | 5 | + | -(green) | + | + | +
14 | S3 | S2 | As close as possible | 1 | - | + | + | + | +
| | | | 2 | - | -(right) | + | -(left) | +
| | | | 3 | -(red) | -(left) | -(left) | -(left) | +
| | | | 4 | -(left) | -(left) | + | + | +
| | | | 5 | - | -(left) | -(red) | -(left) | +
15 | S3 | S1 | As close as possible | 1 | -(left) | + | -(red) | + | +
| | | | 2 | + | - | -(red) | + | +
| | | | 3 | + | - | -(red) | + | +
| | | | 4 | + | -(yellow ) | + | -(left) | -(right)
| | | | 5 | + | + | - | -(left) | +

APPENDIX IV
RESULTS OF EXPERIMENT 2 TESTING LONG COMMANDS BY DIFFERENT SUBJECTS: COMMAND LENGTHS
Test № | Voice owner | Tester | Testing distance | Trial | Commands
Turn the yellow light on | Turn the red light on | Turn the green light on | Make a right click | Make a left click
1 | S1 | S1 | 12 cm | 1 | -(red) | + | + | - (make a left click) | +
| | | | 2 | -(red) | + | + | - (make a left click) | +
| | | | 3 | -(red) | + | + | - (make a left click) | +
| | | | 4 | + | + | + | - (make a left click) | +
| | | | 5 | + | + | + | - (make a left click) | +
2 | S1 | S4 | 12 cm | 1 | - | + | - | - (make a left click) | +
| | | | 2 | - | - | - | - | -
| | | | 3 | - | - | - | - (make a left click) | -
| | | | 4 | + | - | + | - (make a left click) | +
| | | | 5 | - | - | - | - (make a left click) | +
3 | S1 | S2 | 12 cm | 1 | - | - | - | - | +
| | | | 2 | - | + | - | - | -
| | | | 3 | - | - | + | - | -
| | | | 4 | - | - | - | - | -
| | | | 5 | - | - | + | - | -
4 | S1 | S4 | As close as possible | 1 | - | - | -(make a right click) | - (make a left click) | +
| | | | 2 - | | -(make a left click) | -(make a left click) | - (make a left click) | +
| | | | 3 | + | -(green) | - | - (make a left click) | -
| | | | 4 - | | -(make a left click) | - | - (make a left click) | +
| | | | 5 | + | - | - | - (make a left click) | +
5 | S1 | S2 | As close as possible | 1 | -(make a left click) | -(green) | - | - (make a left click) | +
| | | | 2 | - | - | + | - (make a left click) | +
| | | | 3 | - | - | + | - | +
| | | | 4 | - | - | -(make a left click) | - (make a left click) | +

5

+

- (make a
left click)

+
6 | S2 | S2 | 12 cm | 1 | -(red) | + | + | + | +
| | | | 2 | + | + | + | + | +
| | | | 3 | + | + | + | + | +
| | | | 4 | - | -(green) | + | + | +
| | | | 5 | - | + | + | + | +
7 | S2 | S4 | 12 cm | 1 | -(green) | - | + | + | -(make a right click)
| | | | 2 | - | -(make a right click) | + | + | -(make a right click)
| | | | 3 | - | - | - | + | -(make a right click)
| | | | 4 | - | - | + | + | -
| | | | 5 | - | - | + | + | -
8 | S2 | S1 | 12 cm | 1 | -(red) | + | - | - | +
| | | | 2 | -(green) | + | - | - | +
| | | | 3 | - | + | - | - | +
| | | | 4 | - | - | - | - | -
| | | | 5 | -(red) | - | - | - | -
9 | S2 | S4 | As close as possible | 1 | -(red) | + | - | + | -(make a right click)
| | | | 2 | -(red) | -(make a right click) | -(make a right click) | + | -(make a right click)
| | | | 3 | - | + | -(make a right click) | + | -(make a right click)
| | | | 4 | - | + | -(make a right click) | + | -(make a right click)
| | | | 5 | - | + | + | + | +
10 | S2 | S1 | As close as possible | 1 | - | + | -(red) | + | -
| | | | 2 | - | + | -(red) | + | -(make a right click)
| | | | 3 | -(red) | + | + | + | -(make a right click)
| | | | 4 | - | + | -(red) | + | +
| | | | 5 | - | - | -(red) | + | +
11 | S4 | S4 | 12 cm | 1 | + | -(green) | + | - | +
| | | | 2 | + | + | + | + | +
| | | | 3 | + | + | + | + | +
| | | | 4 | + | + | + | + | +
| | | | 5 | + | - | + | + | +
12 | S4 | S2 | 12 cm | 1 | - | + | - | - | -
| | | | 2 | - | + | - | + | +

3

4 | - | + | - | - | -
5 | - | + | - | - | -(make a right click)
13 | S4 | S1 | 12 cm | 1 | + | -(yellow) | -(yellow) | - | -
| | | | 2 | - | -(yellow) | -(yellow) | - | -
| | | | 3 | + | - | -(yellow) | - (make a left click) | -
| | | | 4 | + | - | -(yellow) | - | +
| | | | 5 | + | -(yellow) | - | - | +
14 | S4 | S2 | As close as possible | 1 | - | + | + | - | +
| | | | 2 | - | + | -(yellow) | + | +
| | | | 3 | - | + | - | + | +
| | | | 4 | - | + | - | - (make a left click) | -(make a right click)
| | | | 5 | + | + | - | + | +
15 | S4 | S1 | As close as possible | 1 | + | -(yellow) | -(yellow) | - | +
| | | | 2 | + | - | -(yellow) | - (make a left click) | -(make a right click)
| | | | 3 | + | -(yellow) | -(yellow) | - (make a left click) | +
| | | | 4 | + | -(yellow) | -(yellow) | - (make a left click) | -(make a right click)
| | | | 5 | + | -(yellow) | -(yellow) | - (make a left click) | +

APPENDIX V
RESULTS OF EXPERIMENT 3: ENVIRONMENTAL TESTING

Quiet environment

Street

№ trial | Left mouse | Right click | Open file | Drag and drop | Email reader
1 | + | + | - | + | +
2 | + | + | - | + | +
3 | + | + | + | + | +
4 | - | - | + | + | +
5 | + | - | - | + | +

Coffee shop

№ trial | Left mouse | Right click | Open file | Drag and drop | Email reader
1 | + | + | - | + | +
2 | + | - | + | - | +
3 | + | - | + | - | +
4 | + | + | + | + | +
5 | + | - | + | + | +

Bus stop

№ trial | Left mouse | Right click | Open file | Drag and drop | Email reader
1 | + | + | + | + | +
2 | + | + | + | + | +
3 | - | - | + | + | +
4 | - | - | + | + | -
№ trial | Left mouse | Right click | Open file | Drag n drop | Email reader
1 | + | + | + | + | +
2 | - | - | - | - | +
3 | + | - | + | + | +
4 | + | + | + | + | +
5 | + | - | + | + | +

5 | + | + | + | + | +

Bar

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

Classroom

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

APPENDIX VI
RESULTS OF EXPERIMENT 4: FALSE POSITIVE TESTING
№ trial | Left house | Right blick | Open smile | Dark and drop | Email speeder
1 | - | - | + | + | +
2 | - | + | + | + | +
3 | + | - | + | + | +
4 | + | - | - | + | +
5 | + | + | + | - | +
№ trial | Mouse | Click | File | Drag | Email
1 | + | + | - | -(right click) | +
2 | + | + | - | -(right click) | -
3 | + | + | + | -(right click) | -
4 | + | + | - | - | -
5 | + | + | - | -(right click) | -

APPENDIX VII
RESULTS OF EXPERIMENT 5: DISTANCE TESTING

Distance - bluetooth 1m

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

Distance – bluetooth 2m

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

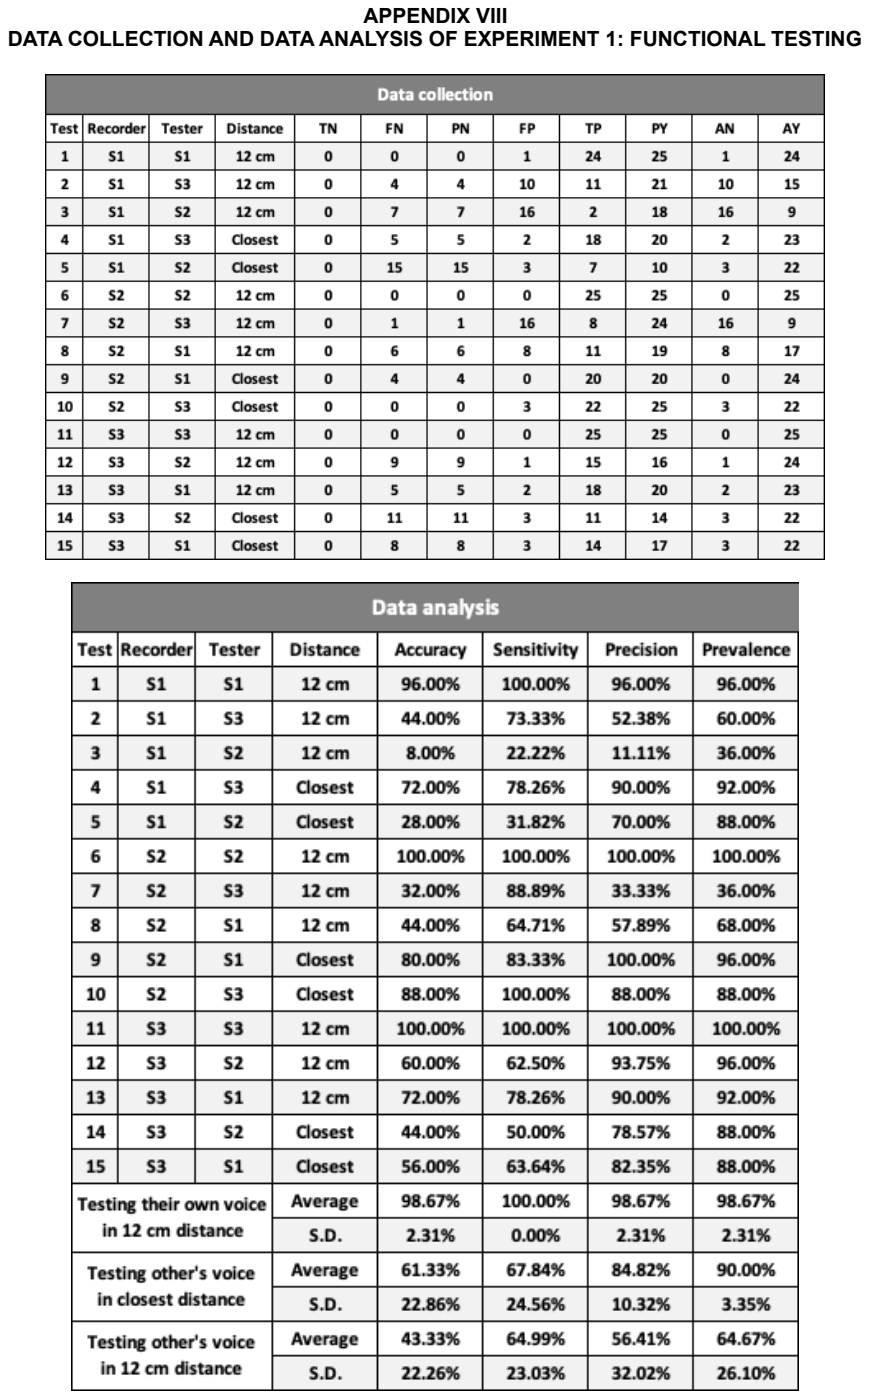
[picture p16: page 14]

APPENDIX VIII
DATA COLLECTION AND DATA ANALYSIS OF EXPERIMENT 1: FUNCTIONAL TESTING

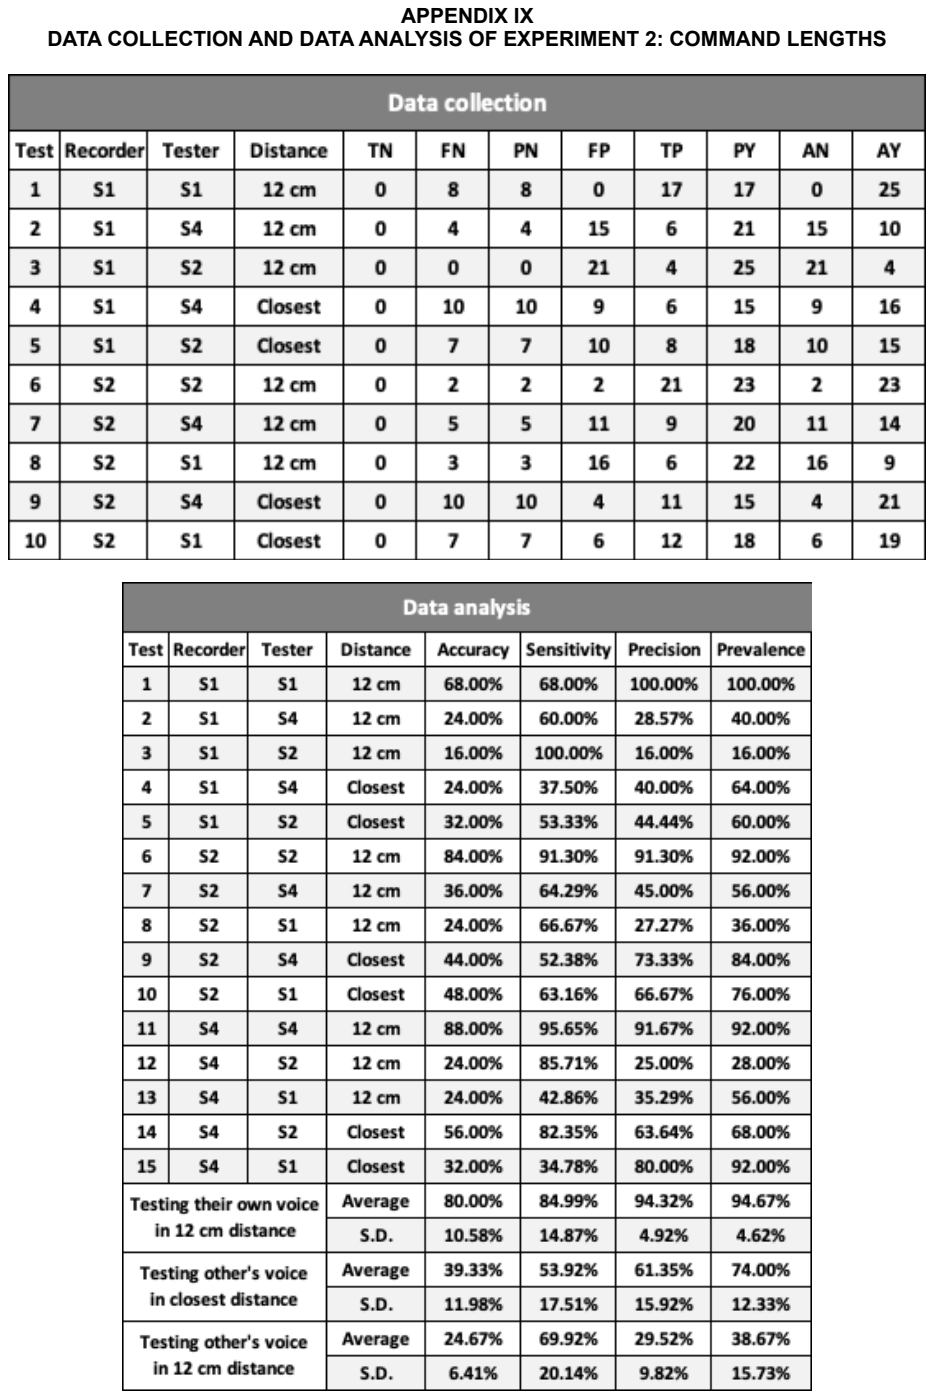
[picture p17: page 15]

APPENDIX IX
DATA COLLECTION AND DATA ANALYSIS OF EXPERIMENT 2: COMMAND LENGTHS

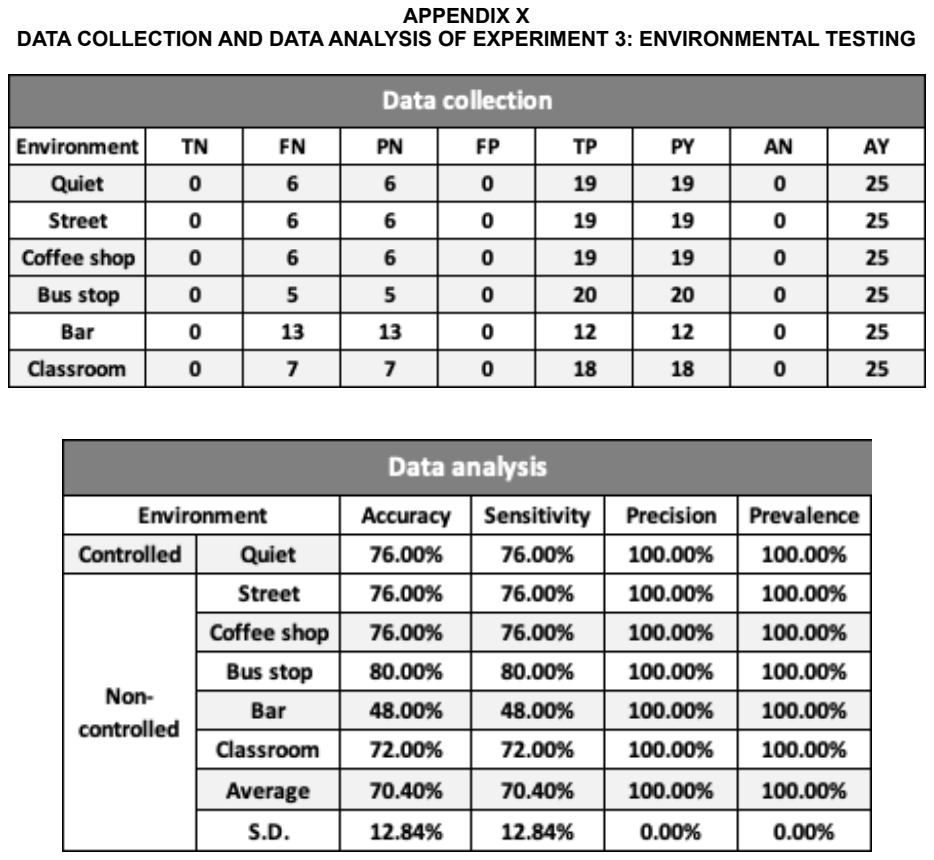
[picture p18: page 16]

APPENDIX X
DATA COLLECTION AND DATA ANALYSIS OF EXPERIMENT 3: ENVIRONMENTAL TESTING

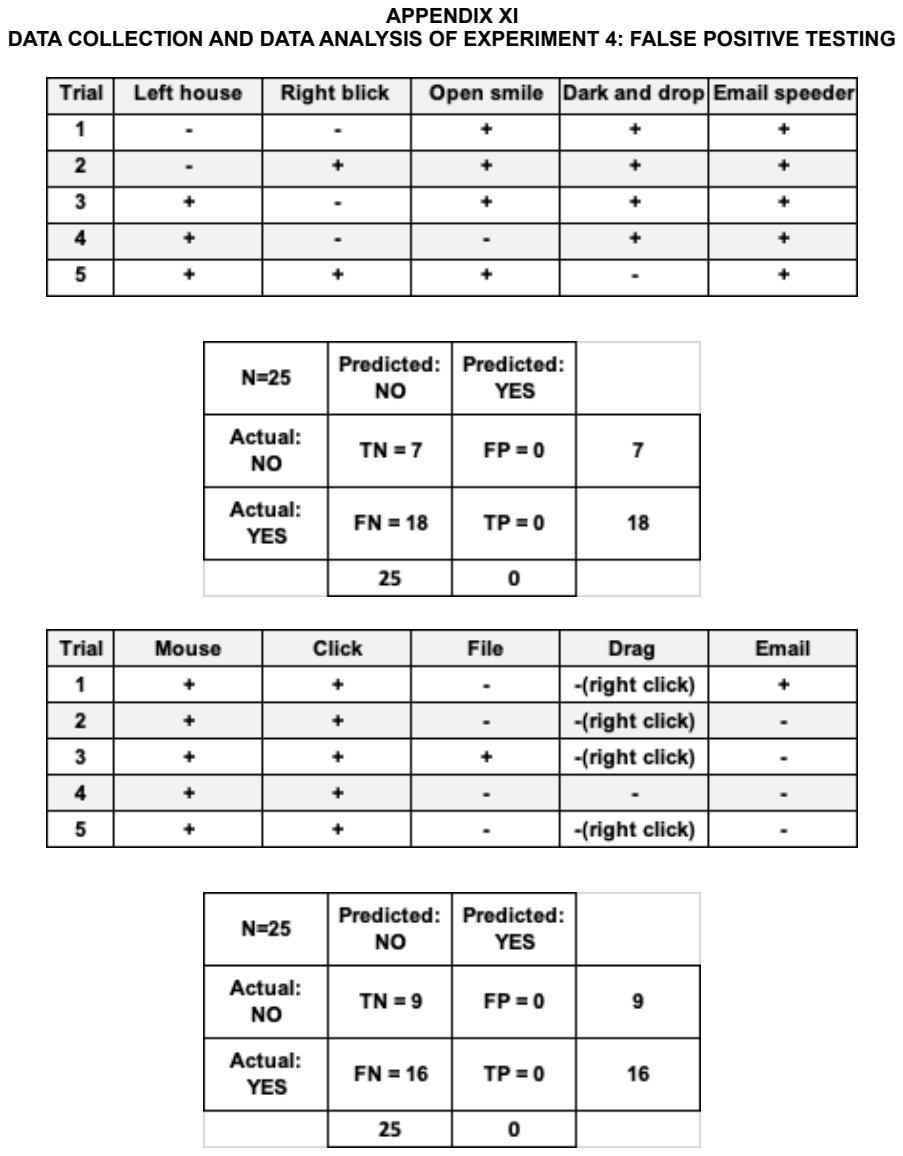
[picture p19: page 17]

APPENDIX XI
DATA COLLECTION AND DATA ANALYSIS OF EXPERIMENT 4: FALSE POSITIVE TESTING

APPENDIX XII
DATA COLLECTION AND DATA ANALYSIS OF EXPERIMENT 5: DISTANCE TESTING

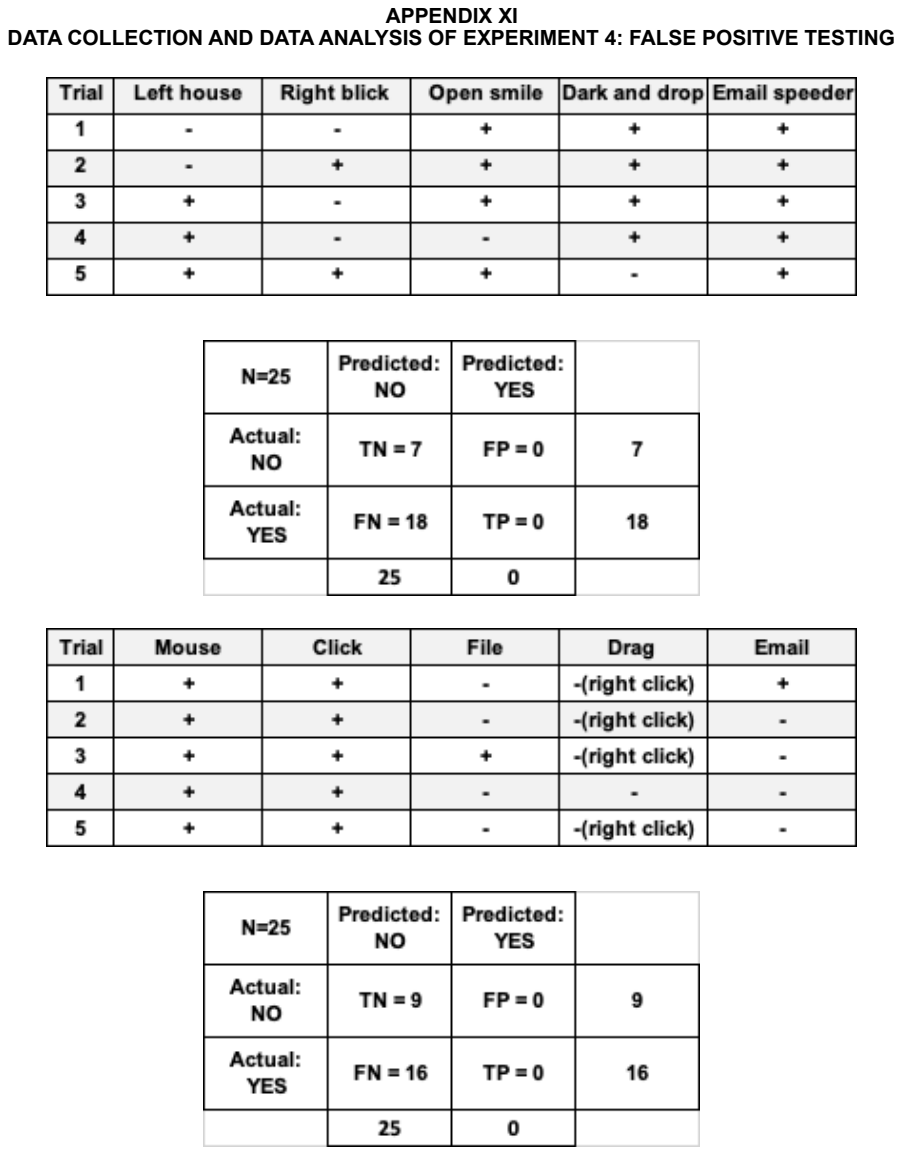
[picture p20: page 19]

APPENDIX XI
DATA COLLECTION AND DATA ANALYSIS OF EXPERIMENT 4: FALSE POSITIVE TESTING

APPENDIX XII
DATA COLLECTION AND DATA ANALYSIS OF EXPERIMENT 5: DISTANCE TESTING

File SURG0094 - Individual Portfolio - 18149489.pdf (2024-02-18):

University College London
RNOH, Brockley Hill, Stanmore, HA7 4LP, UK www.ucl.ac.uk/aspire-create

Centre for Rehabilitation Engineering and Assistive Technology

# Coursework Submission Coversheet

Student Number (not name!): 18149489

Module Code:
SURG0094

Coursework Title:
Groupp Research Project

Submission Deadline:
11/12/2019

Word count (include all sections except references/bibliography and appendices. Exclude footnotes, tables, figures, captions, references/bibliography and appendices):
2290

Feedback Request (optional). Please indicate any area(s) of your coursework submission upon which you would particularly like feedback:

NB: I confirm that by submitting this piece of coursework, I have read and understood the UCL statements and guidelines concerning plagiarism.
UCL Policy on Plagiarism (https://www.ucl.ac.uk/students/exams-and-assessments/plagiarism)
UCL Policy on Late Submission of Coursework (https://www.ucl.ac.uk/academic-manual/chapters/chapter-4-assessment-framework-taught-programmes/section-3-module-assessment)

If you are unable to submit on-time due to extenuating circumstances (EC), please refer to the UCL Policy on Extenuating Circumstances and contact you’re your programme administrator as soon as possible.

UCL Policy on Extenuating Circumstances (https://www.ucl.ac.uk/academic-manual/chapters/chapter-4-assessment-framework-taught-programmes/section-6-extenuating-circumstances)

INDIVIDUAL PORTFOLIO

Week 1

The project brief was designing a device that enables a person with tetraplegia to activate a switch action. Assumptions of the user included: no speech and cognitive impairment, no physical movement below neck, and may be ventilated.

Week 2

On our first meeting as a team, we discussed existing switches that we had gathered before. They include:

a) Sip and puff switch [1]. As the name suggests, the device comprises of a tube which the user can sip and puff into. This device is low cost, easy to wear and requires low power. However, it is hard to control and presumably tire the user’s respiratory system. It requires wire, so it takes more space and makes the design complicated. It also needs regular maintenance and cleaning.
b) Neuronode [2]. It uses electromyography (EMG) as input to activate the switch. It can be placed on any muscle, so it is relatively easy to control. Another advantage is wireless; it uses Bluetooth. However, the device only has 24-hour battery life and is quite expensive. It is also attached on the skin, which may cause problems if used for a long period of time.
c) Emego [3]. It is essentially similar to Neuronode, with added specification which can be used by two people.
d) Nous [4]. Unlike Neuronode and Emego, the device uses electrooculography (EOG), which detects intentional eye blinking. It may interfere with the user’s appearance and visual function.
e) EarFieldSensing [5]. It includes an ear plug which enables the device to detect facial expressions. Since it is quite intrusive, it may cause inconvenience.
f) Twitch Switch [6]. The device is activated by wrinkling of forehead. It may cause false operation if the user involuntarily wrinkles.

Some of the devices are wired, require regular maintenance, and takes time to set-up and operate. A common issue that we found was affordability. To understand the requirements that the device should have, Paporn and I defined the stakeholders involved in the use of switch and predicted their requirements (Table 1).

Table 1. Stakeholders involved in the development and operation of a switch.

Stakeholder | Requirements
Patient | • Easy to use product • Cheap/affordable price • Safe for user • Long lasting product • Reliable • Comfortable • Good appearance • Minimal set up/ removal

Caregiver | • Easy to use product • Simple maintenance • Minimal set up/ removal • Reliable
Family | • Product cost • Simple maintenance • Set up/removal process • Payment can be reimbursed • Warranty
Doctor | • Product specification • Advantages/disadvantages of product • Patient’s condition and prognosis • Patient and family’s preferences • Set up/removal process
Emergency service | • Patient’s condition and prognosis • Removal process • Reliable
Insurance | • Patient’s condition and prognosis • Cheap/affordable price • Reliable • Warranty
Bank | • Patient’s condition and prognosis • Patient’s insurance information • Product specification • Product cost • Financial status of supporter
Supplier | • Product specification • Patient condition
Manufacturer | • Patient condition • Materials • Cost • Ethics and regulation; including standards • Schedule • Funding
Ethics | • Manufacturing process • Product test, clinical test • Standards
Regulator | • Risk assessment • Patient condition • Manufacturing process • Product test, clinical test • Standards
Maintenance service | • Training on how to set up, operate, fix problems • Product specification
Government | • Cost of product; to determine tax • Access to patient information

From the limitations of existing device and requirements of each stakeholder, we conclude that a switch should have the following requirements: portable, wireless, low cost, non-invasive, and easy operation and maintenance. We derived them into technical specification which includes Bluetooth and battery powered. We came up with some ideas:
a) Voice recognition device. The device employs a pre-recorded voice commands to activate actions.
b) Electronic retainer. The idea is to have a thin circuit board in a teeth retainer, so user can activate the switch by biting it. We thought this is a novel idea, but currently we are limited by knowledge and time.
c) Chewing switch. The principle is similar to electronic retainer, but the design is a simple board placed outside the mouth.
d) Touchpad display. It employs a force resistive sensor which can be activated by close proximity.
We decided to choose voice recognition device because it is non-invasive and can use multiple commands. The components will be comprised of a voice recognition module, Bluetooth module and battery. Initial design was to include all components in a box and attach the box to a strap so it can be hanged around the neck.

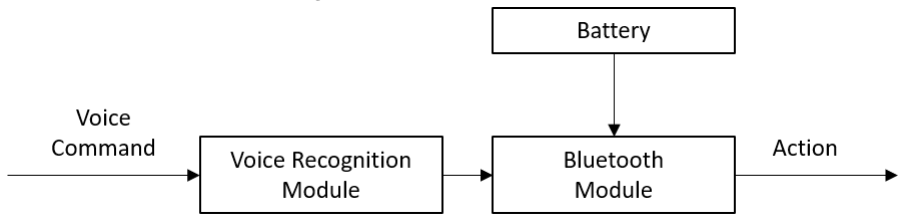
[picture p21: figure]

Figure 1. Diagram representing the major components of voice recognition device.

The major limitation to this device is the reliability of the voice recognition module, because voice recording is sensitive to noise. This problem can be mitigated by use of filter and good quality microphone.
We have not decided team roles yet, but for the next few weeks Federico and Alina would start working on the Bluetooth module, and Paporn and I would learn the basics of Arduino.

Week 3

We had a lecture by Mr Andrew Kell on assistive technology for ICT access. Speech recognition was mentioned in his lecture. The major advantage of speech recognition is it can dictate text. However, there are a lot of commands that user should learn to perform the functions. This idea is similar to our idea, although our device is only a prototype.
This week we bought a Bluetooth module, HC-05. Federico and Alina were working to connect the Bluetooth module to computer.

Week 4

Mr Irving Caplan gave us a lecture on basic electronics and introduction to Arduino, specifically Arduino Uno. I learned how to install the drivers and upload template sketch to the board.

Week 5

I managed to make a circuit to light an LED with Arduino Starter Kit for Beginner by following Arduino Projects Book. The circuit instruction and sketch were provided in the book. Basically, a sketch consists of three parts:
a) The definition of parameters.
e.g. int ledPin = 13; // define the number of LED pin on the breadboard
b) Void setup ()
This part sets what needs to be done only once.
c) Void loop ()
This part contains the commands that will be repeated over and over.

Week 6

We were advised to include stakeholder’s opinion on designing the device. We decided to collect data by questionnaire. Initially, we asked if we could have an interview in Aspire as well, but we could not due to time limit. Paporn and I created two separate questionnaires, one for user and another one for family, caregiver and clinician. The first draft of the questionnaire was intended to specifically asks what user wants from a voice recognition device (Please see Appendix I).
By this week, we still had problem in connecting the Bluetooth module.

Week 7

Since the voice recognition module had not arrived yet, we started to devise alternative options, including sip and puff switch, chin switch and capacitive sensor. A chin switch uses a force sensitive sensor embedded on a tubing with the main component worn around the neck. A capacitive sensor senses when there is an object in close proximity interfering with a self-generated electric field surrounding the sensor. It could be mounted on a flexible tubing close to mouth so it can be gritted or chewed by the user. Finally, we decided on the capacitive sensor because it requires less energy than other options, and the components are readily available on the market. We can use material like silicon rubber to cover the sensor, as it can be moulded easily. It was also decided that I would design the device in CAD.

Week 8

We had a meeting with Andrew and Tom and received feedbacks on our alternative plan. A device that requires contact with mouth has several limitations, including robustness and hygiene. It will be chewed repeatedly, so the protecting cover should have high fatigue strength, high abrasion resistance and long lifetime without limiting the function of the sensor. The device would require regular maintenance because it would be constantly covered in saliva. A suggestion was to put the sensor outside the body as something to wear. Therefore, it would be non-invasive, less conspicuous, and require less maintenance. It is a proximity sensor, so it does not need force or pressure to activate the device.
We also had a solution for Bluetooth problem. It turned out that HC-05 is a serial type Bluetooth module, which is able to transfer files between devices but not to receive keyboard input. We were looking for a Human Input Device (HID) type Bluetooth module, which can translate a user’s input to keyboard and mouse function. Adafruit Feather 32u4, which we previously used in another course, is a HID module. Therefore, it was decided that we would use that module.
There were also comments on the questionnaire. We realised that there were irrelevant questions on the first draft. Our project was clearly intended for ICT access, but we included unrelated questions like asking for other activities that requires assistance. Questions need to be generated carefully so we do not breach ethical considerations regarding personal data. Personal data is regulated under Data Protection Act, which is a translation of European General Data Protection Regulation (GDPR). Therefore, the questionnaires were revised and the final document can be seen in Appendix I of group report. I also learned that engaging stakeholders should be the earliest thing to do to define the problem and user requirements. By the end of this week, Federico managed to make the capacitive sensor to work. He tested the device by himself without any measurement. Therefore, we designed a test to measure the minimum distance for the sensor to activate (Figure 1). I designed several boxes with different thickness: 2, 4, 6, 8 and 10 mm (Figure 2), in Autodesk Inventor.

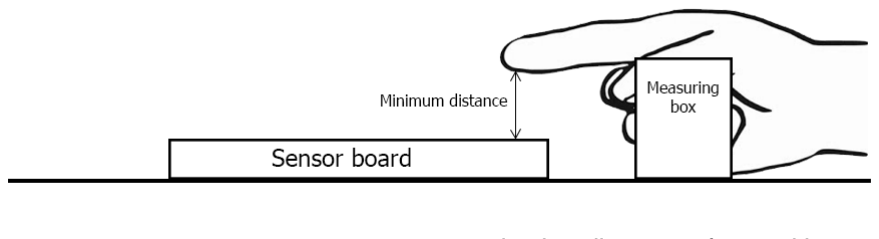
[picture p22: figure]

Figure 2. Test to measure the minimum activation distance of capacitive sensor.

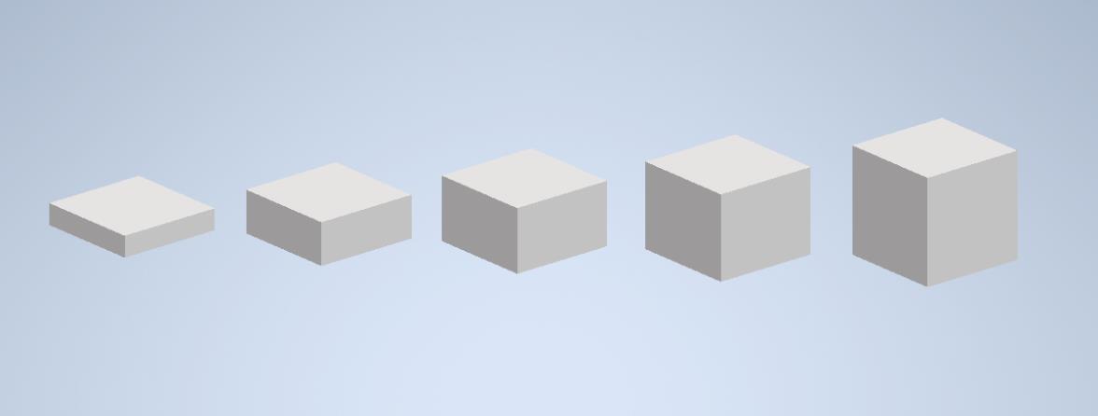
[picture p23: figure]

Figure 3. Measuring boxes.

In the end, we did not do the test because the voice recognition module arrived and we started to focus on that. I started to design the case for the device by modelling each component, voice recognition module and Bluetooth module.

Week 9

Federico finished the voice recognition module connected to Arduino board and powered using a computer. The device could record 3 set of commands, each contains 5 commands, but we had only been able to use 1 set. Using his own voice recorded, Federico was able to activate the device repeatedly from long distance. When the others tried to test it, there were true negative results even in close distance. There were several ways to increase the sensitivity of the device. Possible solutions were using a better microphone and installing another module to attenuate the signal. But due to time limit, we could not further developed it.
I was able to build a simple model of voice recognition module and Bluetooth module, only showing the major parts (Figure 3). Although in the final assembly, I did not use these models. I downloaded template models instead to illustrate them more realistically (Figure 5).

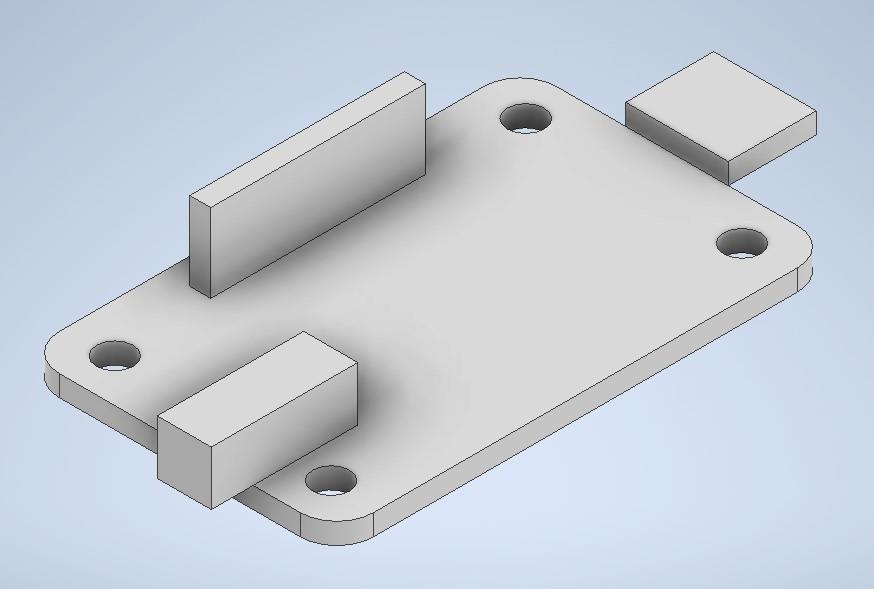
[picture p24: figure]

(a)

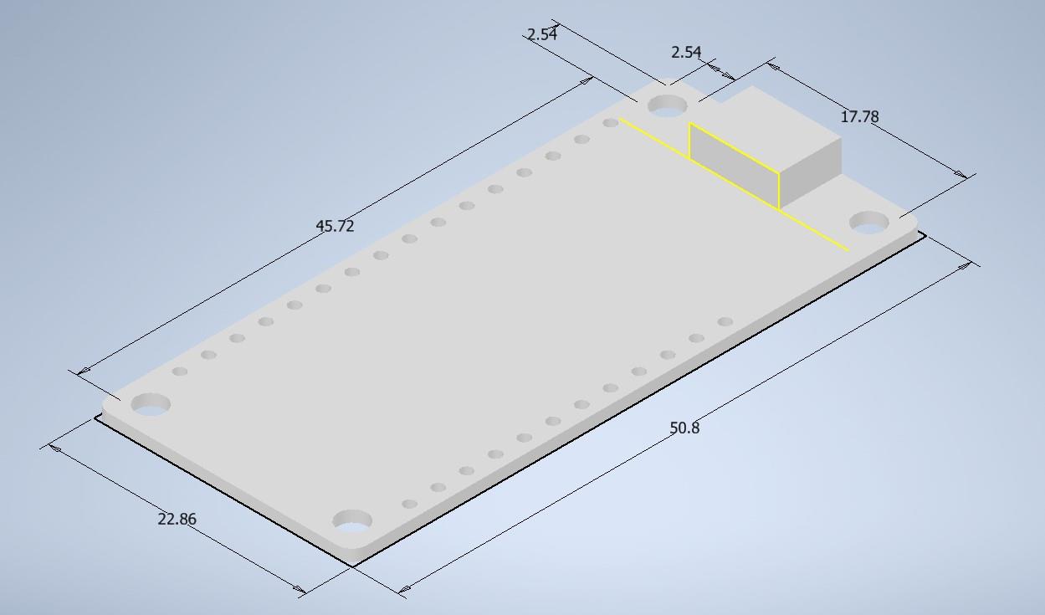
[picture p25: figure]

(b)
Figure 3. (a) Model of voice recognition module. (b) Model of Bluetooth module.

Week 10

The initial design of the case was comprised of a base and a cover. On the base, there were two spaces for Feather and the voice recognition module (Figure 4). The base and its cover were to be connected using screws, hence there were four holes on each side of the board. On the cover, there was a small curvature each on the left and right sides. This was added to help people who wants to open the box, to put their fingers into.

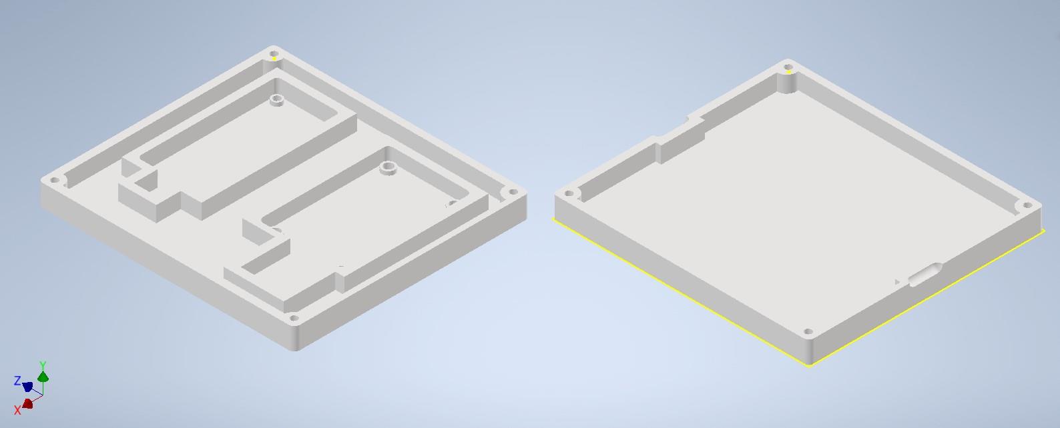
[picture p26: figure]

Figure 4. Initial design of case, comprised of a base (left) and a cover (right).

I revised the design after several considerations. There should be more space for battery and cables. The edges of the cover was protruded and the edges of the base was extruded to attach both boards together (Figure 5). This was done because we have predicted that drilling the screws in may not be done in time. Two supports were made on the left and right sides of the base to attach a strap (Figure 6). Case was printed in Ultimaker 2+ Extended 3D Printer, using acrylonitrile butadiene styrene (ABS). The final product weighed 65 g (Figure 7).


(a)


(b)

Figure 5. Design of the base part of case in (a) orthographic view and (b) perspective view, with Bluetooth module and voice recognition module represented inside. Measurements in mm.

Figure 6. Design of device.


Figure 7. The setup of the case in Ultimaker Cura before being printed.

It turned out that the final device incorporated additional components, namely two batteries, a logic converter and a voltage converter (Figure 8). A logic converter was needed because the Bluetooth module uses a 3.3 V supply and could not define the voice recognition which uses a 5V supply. A voltage converter reduced the voltage from the 9V battery so the voice recognition module and logic converter received suitable values.


Figure 8. Circuit diagram of the device.

The case design did not leave adequate tolerance for space, so we had to fit everything inside. The 9V battery was placed outside. Ideally, the case shall be completely enclosed, leaving only holes for a microphone and a USB cable. The base thickness should also be increased to allow screws inside. Future iteration of this device shall also have a display of battery level, with an increased dimension in mind due to additional component. Overall, planning should be done in advanced and other factors like facility opening times should be predicted. It took about 8.5 hours to print one set of case, so the printing process alone already takes one to two days.
In the same week, Paporn and Alina set some experiments to test the functionality of the device. In all tests, each command was tested 5 times.
a) Experiment 1. Each person recorded 5 short commands and tested each command in 12 cm distance from the device. Then the other people who did not have their voice recorded tested the commands, in closest distance and 12 cm distance.
b) Experiment 2. This was similar to experiment 1, but the commands were longer.
From these two experiments, it was found that shorter commands have higher accuracy, sensitivity and precision than longer commands. That was why the final prototype used shorter commands. We used two words instead of one word because it will unlikely appear in our conversation. The commands were defined as follows:
- Left mouse – corresponds to left click
- Right click – corresponds to right click
- Open file – corresponds to double click
- Drag and drop – corresponds to left click and holding it for 0.5 seconds
- Email reader – corresponds to opening email
The following tests were developed to test the final commands:
c) Environmental testing. This test was done by one person who recorded the voice, and tested in 12 cm distance. The only variable was environment: controlled and non-controlled. In controlled environment, noise level was kept to minimum. In non-controlled environment, several settings were used: street, coffee shop, bus stop, bar and classroom. In general, the results for non-controlled environment were less accurate and less sensitive than controlled environment.
d) False Positive Testing. We used 2 different sets of command which were similar in sound to the original set of command. The device still activated even if it was not the original command, so it still could not distinguish between similar words.
e) Distance between Bluetooth and computer. We tested the device 1 m and 2 m away from the computer. The results showed that closer distance (1 m) produced higher accuracy and sensitivity.

REFERENCES

[1] Origin Instruments, “Sip and Puff Switch Solutions”,
url: https://www.orin.com/access/sip_puff/
[2] Control Bionics, “Neuronode Trilogy”, url: https://www.controlbionics.com/neuronode/
[3] GSPK Design Ltd., “Emego”, url: emego.co.uk
[4] Thought-Wired Ltd., url: https://getnous.app/
[5] D. J. C. Matthies, B. A. Strecker, B. Urban, “EarFieldSensing: A Novel In-Ear Electric Field Sensing to Enrich Wearable Gesture Input through Facial Expressions,” CHI Conference on Human Factors in Computing Systems, pp. 1911-1922, 2017.
[6] RehabMart, LLC, “The Twitch Activated Assistive Technology Switch”, url: https://www.rehabmart.com/product/the-twitch-activated-assistive-technology-switch-32088.html

APPENDIX I
SURVEY OF ASSISTIVE TECHNOLOGY FOR TETRAPLEGIC USER
1. What is your age?
- 20 and below
- 21 - 30
- 31 - 40
- 41 - 50
- 51 - 60
- above 60
2. What is your current living situation?
- Living alone
- Living with family
- Living with caregiver
- Living with other, please specify: ____________
3. Do you need any assistant in performing activities of daily living?
- Yes
- No
4. If yes, please indicate activities that require an assistant
- Personal hygiene
- Dressing
- Eating
- Toileting
- Transferring/Mobility
- Environment controlling e.g. turn on the light
- Accessing ICT
e.g. using mobile phone
- Other, please specify: ___________________
5. Please indicate if you have difficulty in the following functions
- Head movement e.g. nodding
- Eye twitching or blinking
- Mouth gripping
- Speaking
6. What is your current method to trigger a switch action e.g. turning on computer? ___________________________________________________________________
7. Why you decide to use the current method? ___________________________________________________________________

8. Are you aware of assistive technology that can allow you to trigger a switch action by yourself?
- Yes
- If yes, have you ever try it? ________________________________________________________
- No
- If no, are you interested in trying it? ________________________________________________________
9. Do you have any design preferences of an assistive device for accessing information? e.g. monitor that can detect eye blinking ___________________________________________________________________
10. What are the main factors affecting your choice? ___________________________________________________________________
11. Have you ever used voice recognition technology to trigger some action?
- Yes
- If yes, what do you think about it? ________________________________________________________
- No
- If no, are you interested in trying it? ________________________________________________________
12. What are the advantages and disadvantages in your opinion? ___________________________________________________________________ ___________________________________________________________________
13. How often do you think the battery of the assistive device should be charged?
a. Daily
b. 2 - 3 days
c. 4 - 5 days
d. Weekly
14. How much would you be willing to spend on a voice recognition device? ___________________________________________________________________
15. Do you have any other comments? ___________________________________________________________________ ___________________________________________________________________ ___________________________________________________________________

SURVEY OF ASSISTIVE TECHNOLOGY FOR RELATIVES AND CLINICIANS

1. Please indicate who is completing this survey
- Patient’s family/relatives
- Caregiver
- Doctor
- Other health professional, please specify: _________
2. What is your age?
- 20 and below
- 21 - 30
- 31 - 40
- 41 - 50
- 51 - 60
- above 60
3. How long have you been working/living with tetraplegic patient?
- Less than 1 year
- 1 – 2 years
- 3 – 4 years
- 5 years and above
4. Do you face any difficulty working/living with tetraplegic patient?
- Yes
- If yes, please specify the difficulty ________________________________________________________
- No
5. Does tetraplegic patient require any assistance from you?
- Yes
- If yes, please indicate the activities that require your assistance ________________________________________________________
- No
- If no, is there any other assistant for the patient? ________________________________________________________
6. Have you ever heard about assistive technology?
- Yes
- If yes, please specify what you know about it ________________________________________________________
- No
7. Do you think assistive technology is necessary for a tetraplegic patient?
- Yes
- If yes, please elaborate why you think it is necessary

____________________________________________________

- No

- If no, please explain why you think it is unnecessary ____________________________________________________
8. Have you ever use assistive technology with your patient/relative?
- Yes
- If yes, please specify the type of assistive technology used ________________________________________________________
- No
9. Do you think it is good to enable tetraplegic patient to trigger some action by themselves using assistive technology instead of an assistant?
- Yes
- No
10. Are you aware of assistive technology that can allow patients to trigger a switch action by themselves?
- Yes
- If yes, have you ever used it on your relative/patient? ________________________________________________________
- No
- If no, are you interested in trying it with your relative/patient? ________________________________________________________
11. What do you think is the most challenging issue for tetraplegic patient in terms of triggering some action by themselves? e.g. turn on the light ___________________________________________________________________
12. Do you have any design preferences of assistive technology to trigger an action? e.g. monitor that can detect eye blinking ___________________________________________________________________
13. What do you consider in choosing an assistive technology to trigger an action for your patient/relative?
___________________________________________________________________
14. Have you ever used voice recognition technology to trigger some action?
- Yes
- If yes, what do you think about it? ________________________________________________________
- No
- If no, are you interested in trying it? ________________________________________________________
15. What are the advantages and disadvantages in your opinion? ___________________________________________________________________ ___________________________________________________________________
16. How often do you think the battery of the assistive device should be charged?
- Daily
- 2 - 3 days
- 4 - 5 days
- Weekly

17. How much would you be willing to spend on a voice recognition device? ___________________________________________________________________
18. Do you have any other comments? ___________________________________________________________________ ___________________________________________________________________ ___________________________________________________________________

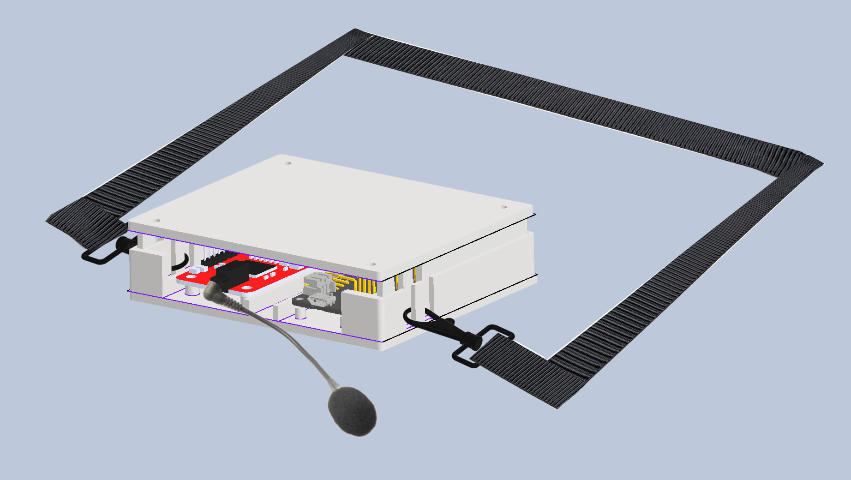
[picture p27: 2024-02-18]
3D drawing/Device design.jpg

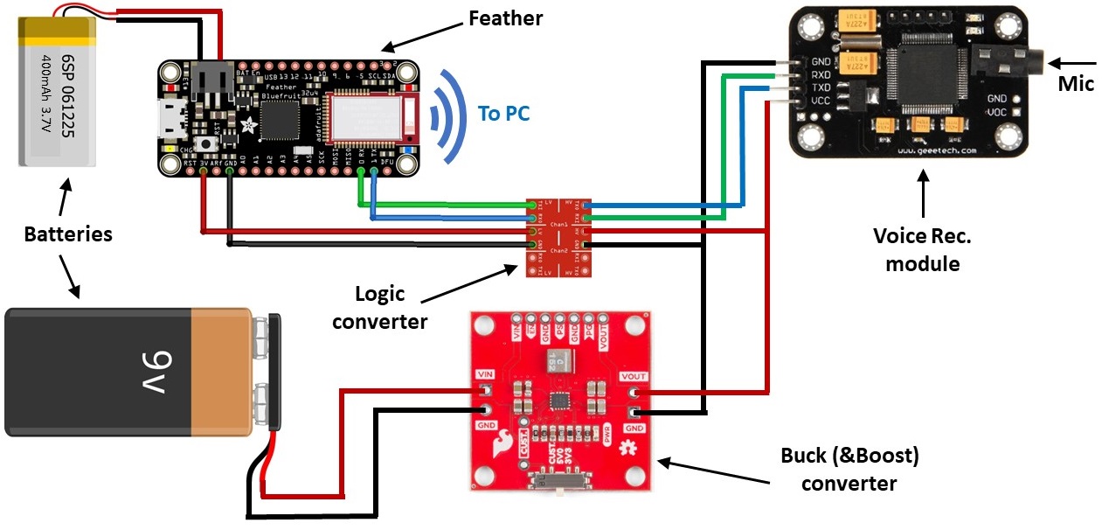
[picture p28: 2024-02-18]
Hardware/el_diagram.jpg

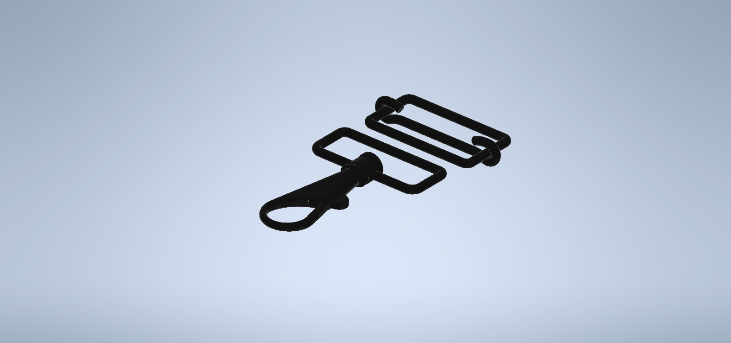
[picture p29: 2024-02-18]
3D drawing/hook2.png

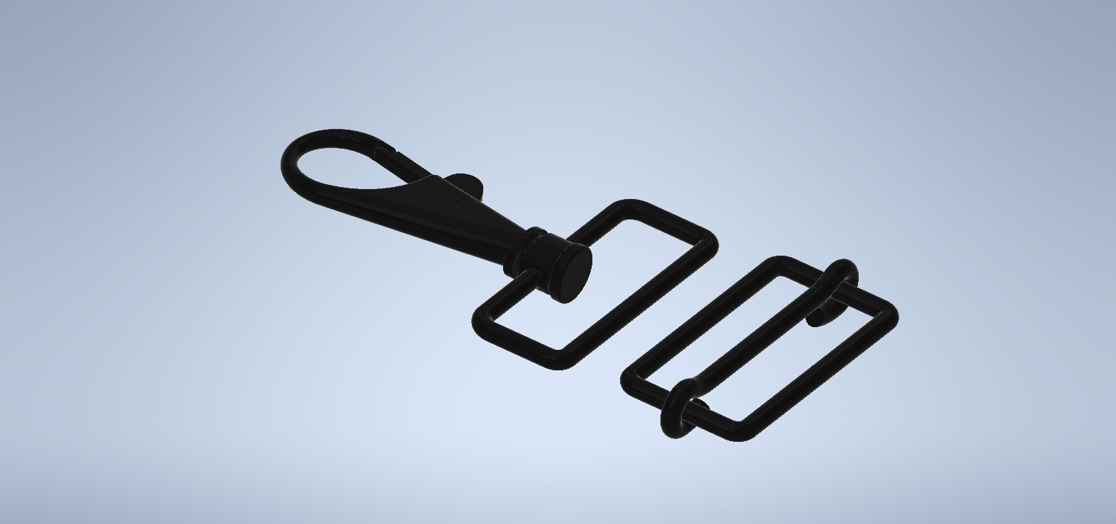
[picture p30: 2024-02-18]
3D drawing/hook1.png

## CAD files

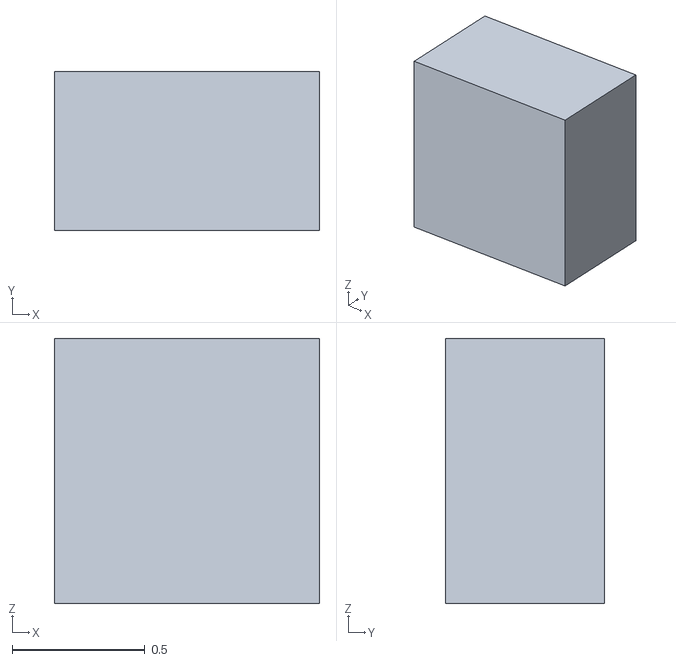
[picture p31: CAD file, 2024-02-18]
3D drawing/Box 6mm.stl
1.00 x 0.6 x 1.00

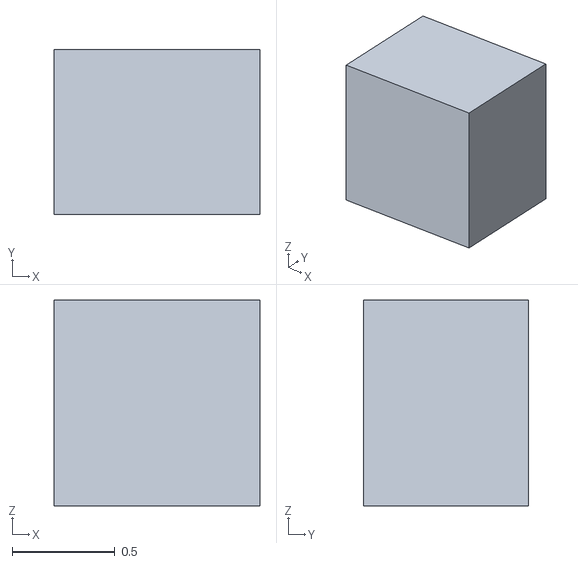
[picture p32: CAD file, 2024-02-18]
3D drawing/Box 8mm.stl
1.00 x 0.8 x 1.00

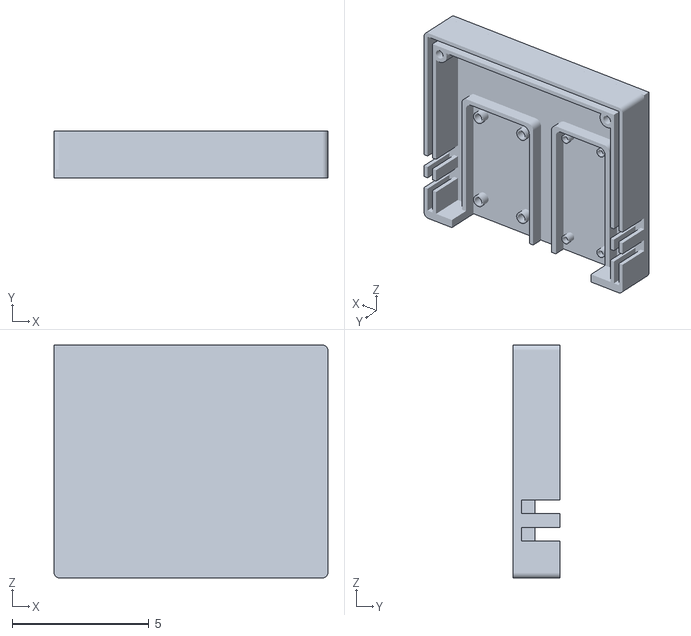
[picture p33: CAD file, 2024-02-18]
3D drawing/Part1.stl
10.0 x 1.70 x 8.50

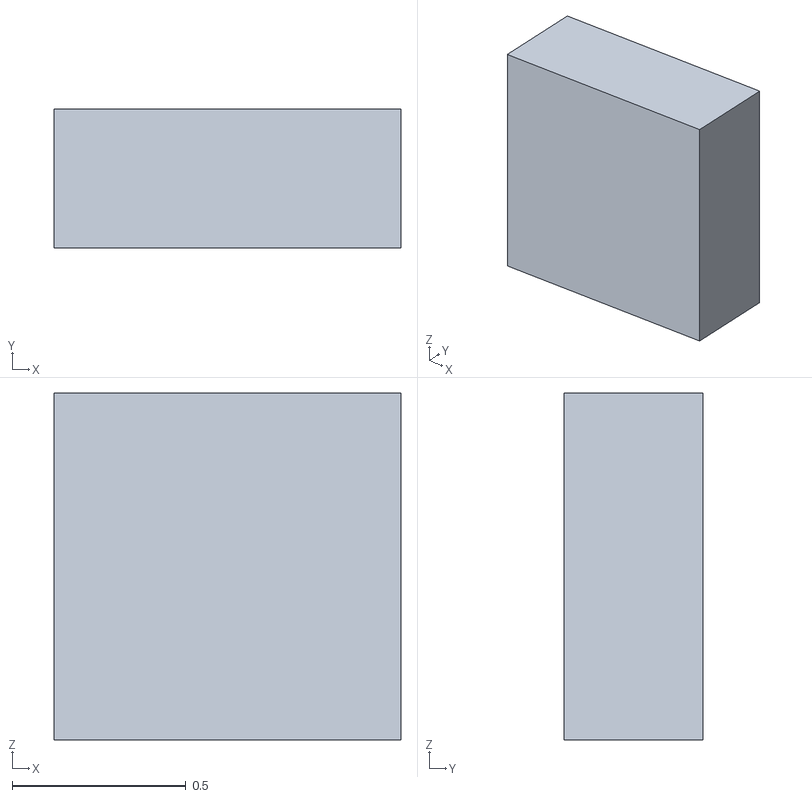
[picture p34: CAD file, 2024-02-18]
3D drawing/Box 4mm.stl
1.00 x 0.4 x 1.00

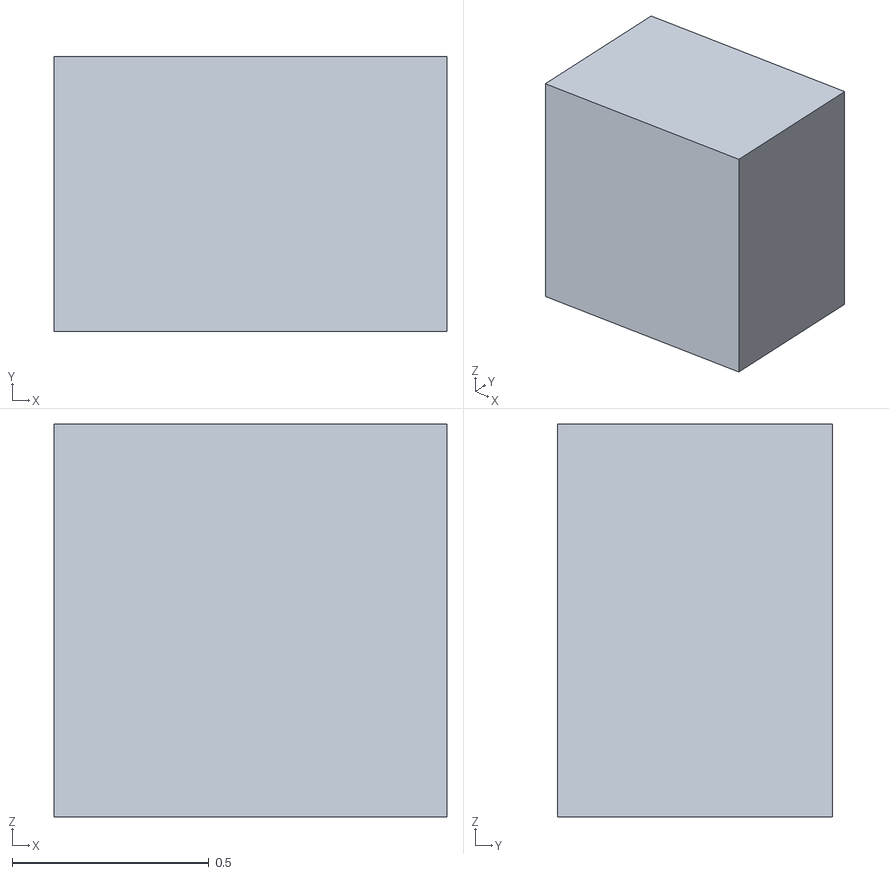
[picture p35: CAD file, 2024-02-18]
3D drawing/Box 7mm.stl
1.00 x 0.7 x 1.00

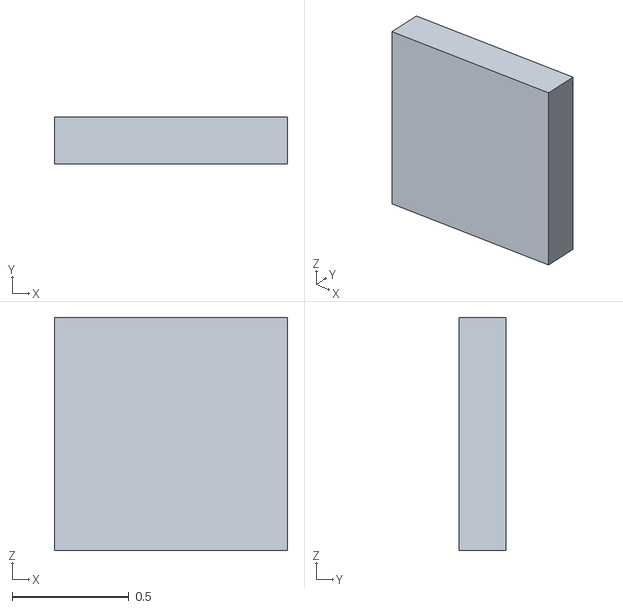
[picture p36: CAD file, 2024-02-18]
3D drawing/Box 2mm.stl
1.00 x 0.2 x 1.00

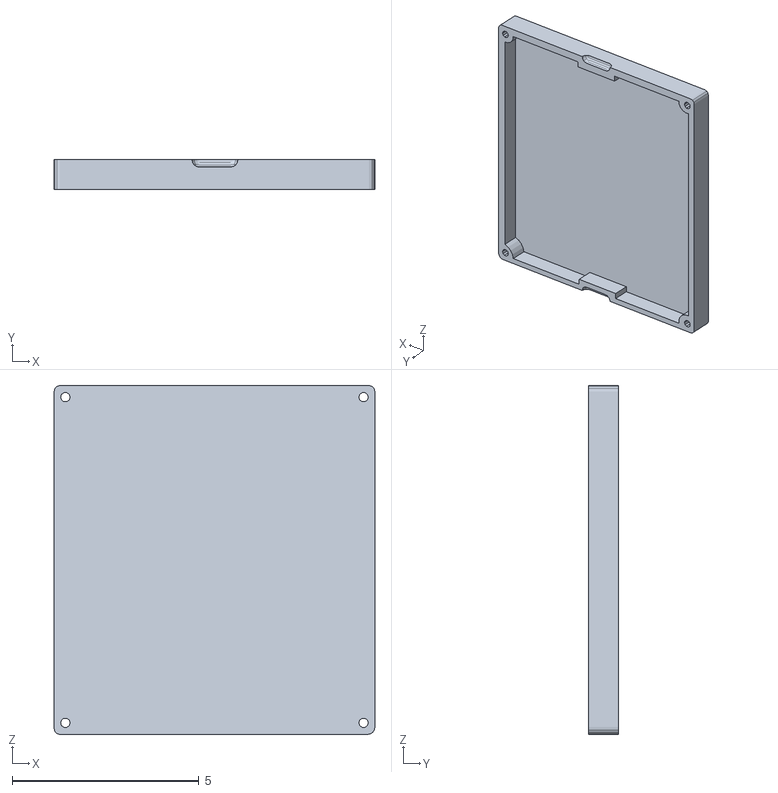
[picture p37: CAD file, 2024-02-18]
3D drawing/Case Cover rev.0.stl
8.59 x 0.8 x 9.34

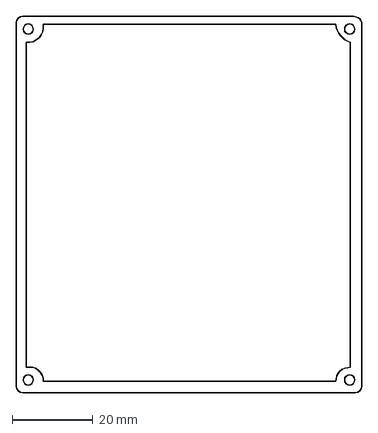
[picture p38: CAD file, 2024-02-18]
3D drawing/Case 1 - face.dxf
85.9 x 93.4 mm

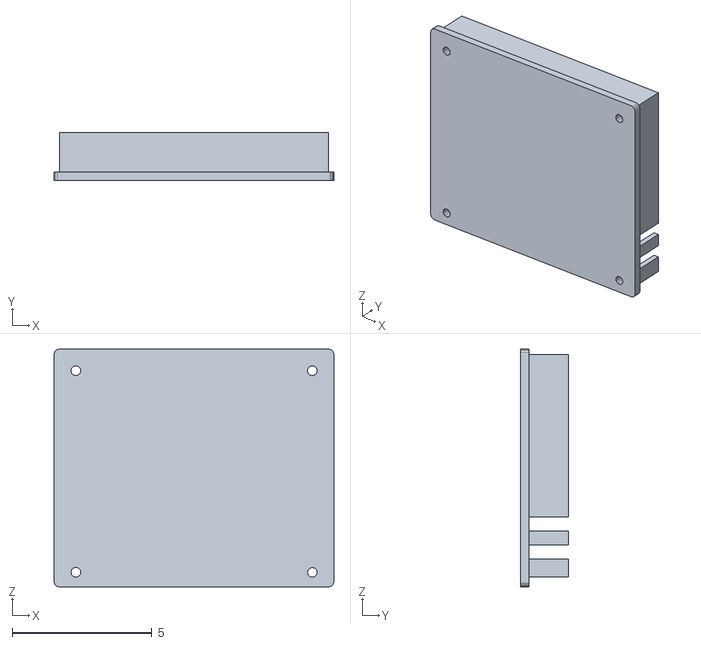
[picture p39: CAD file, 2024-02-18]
3D drawing/Part2.stl
10.0 x 1.70 x 8.50

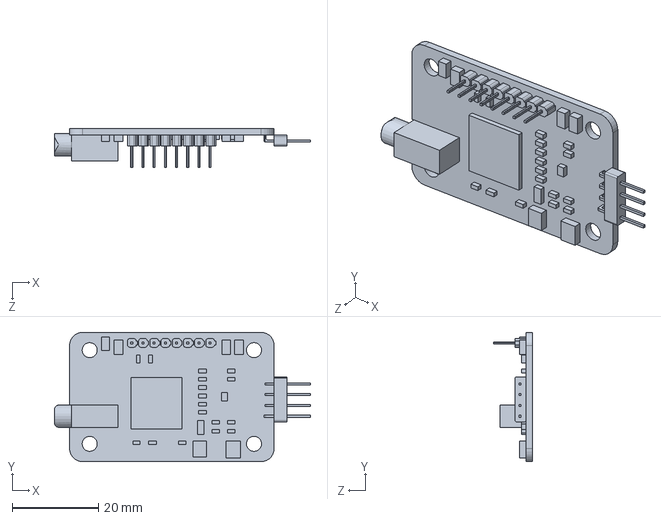
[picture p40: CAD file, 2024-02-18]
3D drawing/Voice Recognition Module.SLDPRT
59.5 x 30.0 x 9.00 mm

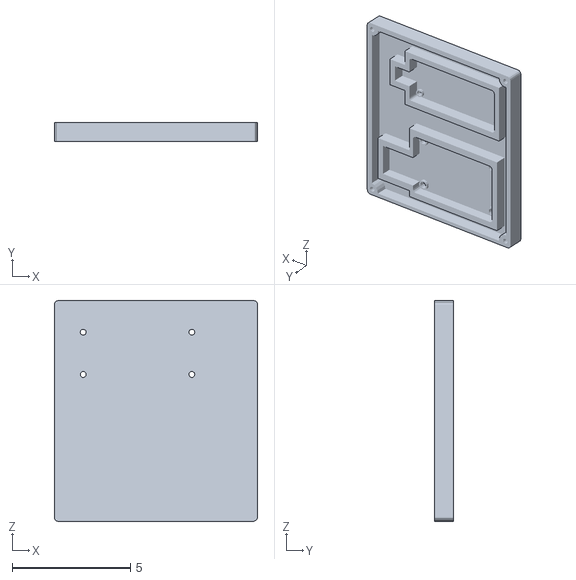
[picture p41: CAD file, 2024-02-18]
3D drawing/Case rev.0.stl
8.59 x 0.8 x 9.34

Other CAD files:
3D drawing/Assembly2.dwg
3D drawing/Face 1.dwg
3D drawing/2829 Adafruit Feather Bluefruit 32u4.f3d
3D drawing/Adafruit Feather 32u4.ipt
3D drawing/Adafruit Feather Bluefruit 32u4 v1.ipt
3D drawing/Assembly1.iam
3D drawing/Assembly2.iam
3D drawing/Box 2mm.ipt
3D drawing/Box 4mm.ipt
3D drawing/Box 6mm.ipt
3D drawing/Box 7mm.ipt
3D drawing/Box 8mm.ipt
3D drawing/Case 1 Cover.ipt
3D drawing/Case 1.ipt
3D drawing/Case Cover new.ipt
3D drawing/Case Cover rev.0.ipt
3D drawing/Case new.ipt
3D drawing/Case rev.0.ipt
3D drawing/Case rev.1.ipt
3D drawing/Part1.ipt
3D drawing/Part2.ipt
3D drawing/Switch Assembly.iam
3D drawing/Voice Recognition Module.ipt
3D drawing/voice recognition.ipt

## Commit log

2024-02-18 Adding experiment testing data
    [Data analysis 3.xlsx]
2024-02-18 Adding 3d drawings of device
    [2829 Adafruit Feather Bluefruit 32u4.f3d, Adafruit Feather 32u4.ipt, Adafruit Feather Bluefruit 32u4 v1.ipt, Assembly1.iam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]
